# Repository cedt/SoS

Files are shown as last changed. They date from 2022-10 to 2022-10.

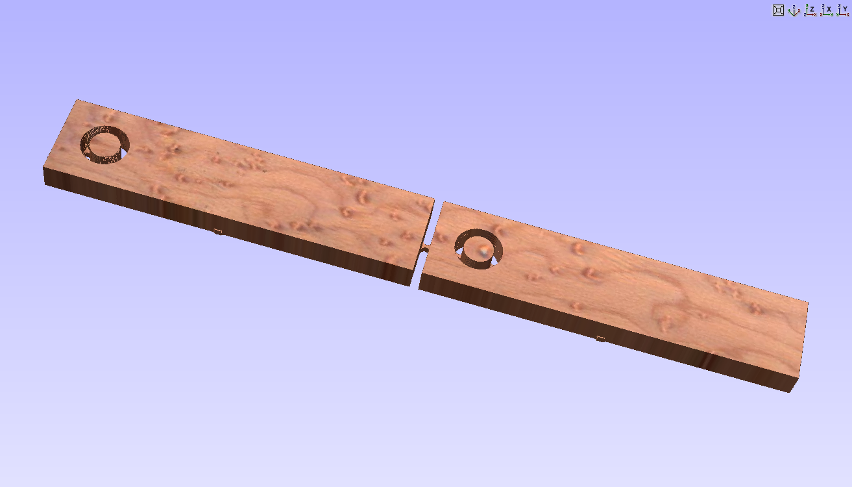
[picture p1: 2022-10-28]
Structure/Structure Type 1/via.png

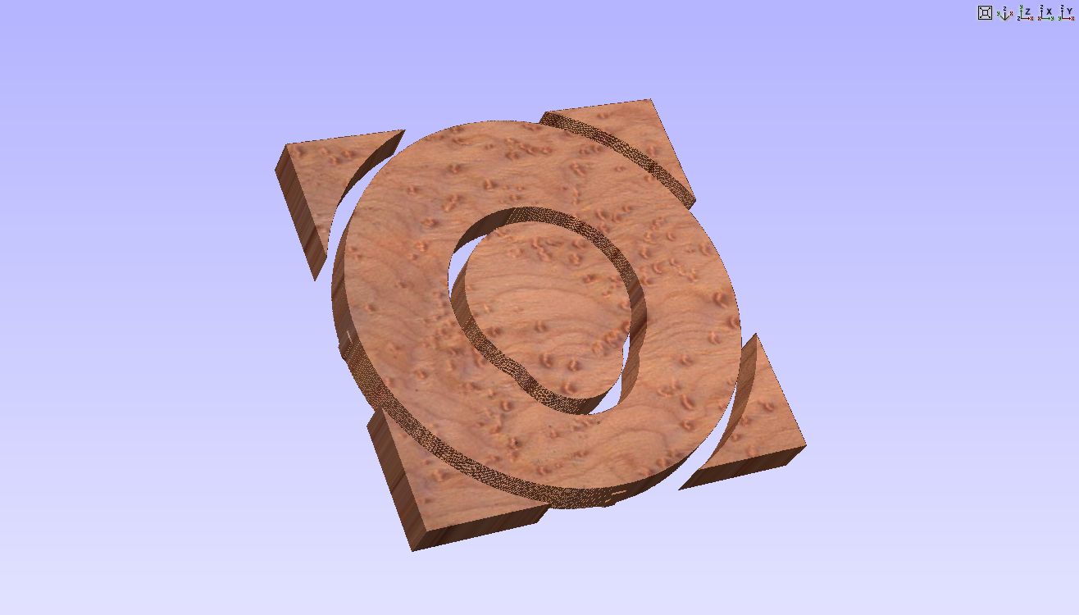
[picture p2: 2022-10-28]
Structure/Structure Type 1/flange.png

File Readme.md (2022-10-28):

# Science on a Stick 

---

### Folder Structure 
```
.
├── Arduino Code 				→ Contains code to be uploaded to Arduino 
│   └── SOS_Arduino_code
│       └── SOS_Arduino_code.ino
├── Arduino PCB and Hardware			→ Contains Schematic, BOM etc
│   ├── BOM-magnetic_switch_sos_v1-2022.pdf	→ Bill of Materials for Reed switch circuit
│   ├── BOM-ScienceonStick_V7-April2022.pdf	→ Bill of Materials for Main PCB
│   ├── Hardware_Acquisition_Sources.docx	→ Suggested sources to acquire components
│   ├── magnetic_switch_sos_v1-2022.sch 	→ Circuit for trigger switch
│   ├── photogate-sos-v2-2022.brd
│   ├── photogate-sos-v2-2022.sch
│   ├── ScienceOnStick_V7-April2022.brd
│   └── ScienceOnStick_V7-April2022.sch 	→ Circuit for main PCB
├── Images and Photographs
│   └── plots
│       └── ... plots created using experiments ... 
├── Python Code
│   ├── Analysis.ipynb
│   └── SoS_Acquisition.py
└── Structure
    ├── Structure Type 1
    │   ├── bar_inside.sbp
    │   ├── bar_outside.sbp
    │   ├── bars.crv
    │   ├── bars.png
    │   ├── base.crv
    │   ├── base_outside.sbp
    │   ├── base.png
    │   ├── flange.crv
    │   ├── flange_inner.sbp
    │   ├── flange_outside.sbp
    │   ├── flange.png
    │   ├── inside.sbp
    │   ├── via.crv
    │   ├── via_inside.sbp
    │   ├── via_outside.sbp
    │   └── via.png
    └── Structure Type 2
        ├── base.crv
        ├── base.png
        ├── correction.sbp
        ├── inside_baseandvia.sbp
        ├── outer_baseandvia.sbp
        ├── stand.crv
        ├── stand_in.sbp
        ├── stand_out.sbp
        ├── stand.png
        ├── via.crv
        ├── VIA-INNER.LOG
        ├── via-inner.sbp
        ├── VIA_OUTER.LOG
        ├── via_outer.sbp
        └── via.png
 ```

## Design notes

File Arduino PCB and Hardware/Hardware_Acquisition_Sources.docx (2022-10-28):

The Structural components of experimental setup can be made using household items such as cardboard, pipes and clothes pins. The electronic components can be acquired from places stated below:

The entire Science on a Stick experiment kit can be bought from https://store.sincgrid.com/index.php?route=product/product&path=71&product_id=108

Individual components can also be acquired as per convenience

1. Arduino Nano: https://www.sparkfun.com/products/15590, https://store-usa.arduino.cc/products/arduino-nano?selectedStore=us
2. Reed switch: https://www.sparkfun.com/products/8642
3. 2 pin Molex connector (M02 Connector): https://www.sparkfun.com/products/9918 (https://www.sparkfun.com/products/9918%20%20)
4. 3 pin Molex connector (M03 Connector): https://www.sparkfun.com/products/retired/9919
5. 36 SWG enamelled Copper wire: https://www.amazon.com/BNTECHGO-AWG-Magnet-Wire-Transformers/dp/B07JBQQR38/ref=sr_1_1_sspa?crid=P3E3WLDIDLN9&keywords=magnet+wire+32+awg&qid=1666948092&qu=eyJxc2MiOiIxLjg1IiwicXNhIjoiMS43MiIsInFzcCI6IjEuNDQifQ%3D%3D&sprefix=magnet+wire+32+aw%2Caps%2C335&sr=8-1-spons&psc=1
6. USB Type A to Mini B: https://www.adafruit.com/product/260
7. 12mm diameter Neodymium magnet: https://www.adafruit.com/product/9

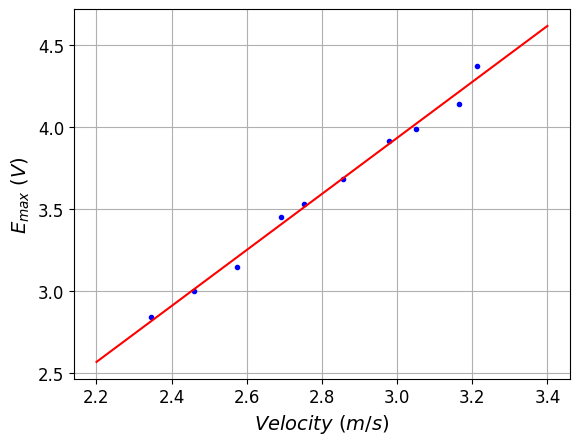
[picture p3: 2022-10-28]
Images and Photographs/plots/peak_V_vs_velocity.png

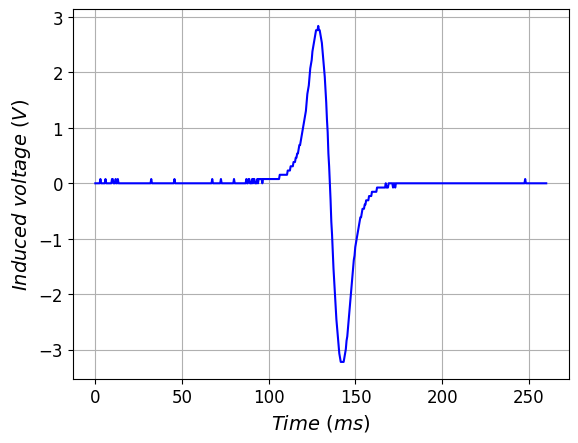
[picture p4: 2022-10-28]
Images and Photographs/plots/V_vs_t.png

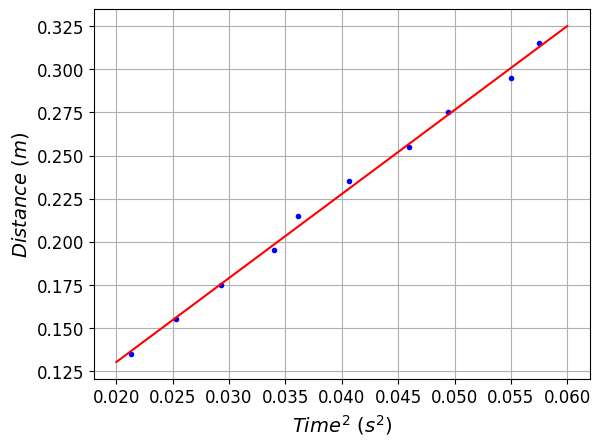
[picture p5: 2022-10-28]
Images and Photographs/plots/distance_vs_t2.png

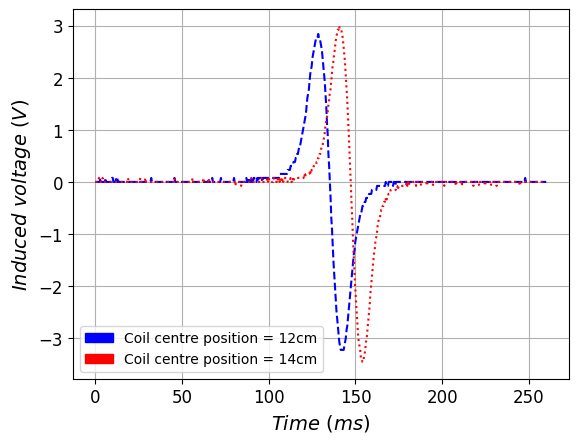
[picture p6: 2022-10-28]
Images and Photographs/plots/V_vs_t_compare.png

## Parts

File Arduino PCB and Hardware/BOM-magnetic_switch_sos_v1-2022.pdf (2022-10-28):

# Bill of Material for Magnetic Switch

Part | Value | Device | Package
LED1 | RED | LED3MM | LED3MM
P-ON | RED | LED3MM | LED3MM
R1 | 1K | RESISTOR | 0207/7 (1/8 Watt)
R2 | 1K | RESISTOR | 0207/7 (1/8 Watt)
R3 | 4.7k | RESISTOR | 0207/7 (1/8 Watt)
S1 | NA | Reed Switch
SL1 | NA | M03-Connector | Male Connector. Right Angle

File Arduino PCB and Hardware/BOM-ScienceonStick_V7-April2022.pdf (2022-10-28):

# Bill of Material for Science on a Stick Arduino Board

Part | Value | Device | Package
C1 | 0.1uF | Ceramic CAPACITOR | C025-025X050
C3 | 0.1uF | Ceramic CAPACITOR | C025-025X050
C4 | 10uF | Electrolytic CAPACITOR | E2,5-6
C5 | 10uF | Electrolytic CAPACITOR | E2,5-6
IC1 | LM358N | LM358N | DIL08
LED1 | RED | LED3MM | LED3MM
LED2 | RED | LED3MM | LED3MM
TOP-SWITCH | NA | M03-Connector | Male Connector
R1 | 680 | RESISTOR | 0207/7 (1/8 Watt)
R2 | 10k | RESISTOR | 0207/7 (1/8 Watt)
R3 | 47k | RESISTOR | 0207/7 (1/8 Watt)
R4 | 47k | RESISTOR | 0207/7 (1/8 Watt)
R5 | 1k | RESISTOR | 0207/7 (1/8 Watt)
R6 | 10k | RESISTOR | 0207/7 (1/8 Watt)
R8 | 4.7k | RESISTOR | 0207/7 (1/8 Watt)
BOTTOM-SWITCH | NA | M03-Connector | Male Connector
S1 | NA | Omron Push-Button | 40-XX
SL1 | NA | 2-pin header | Straight
SL2 | NA | 2-pin header | Straight
COIL | NA | M02-Connector | Male Connector
SL4 | NA | 2-pin header | Straight
U$1 | NA | ARDUINO_NANO | ARDUINO_NANO

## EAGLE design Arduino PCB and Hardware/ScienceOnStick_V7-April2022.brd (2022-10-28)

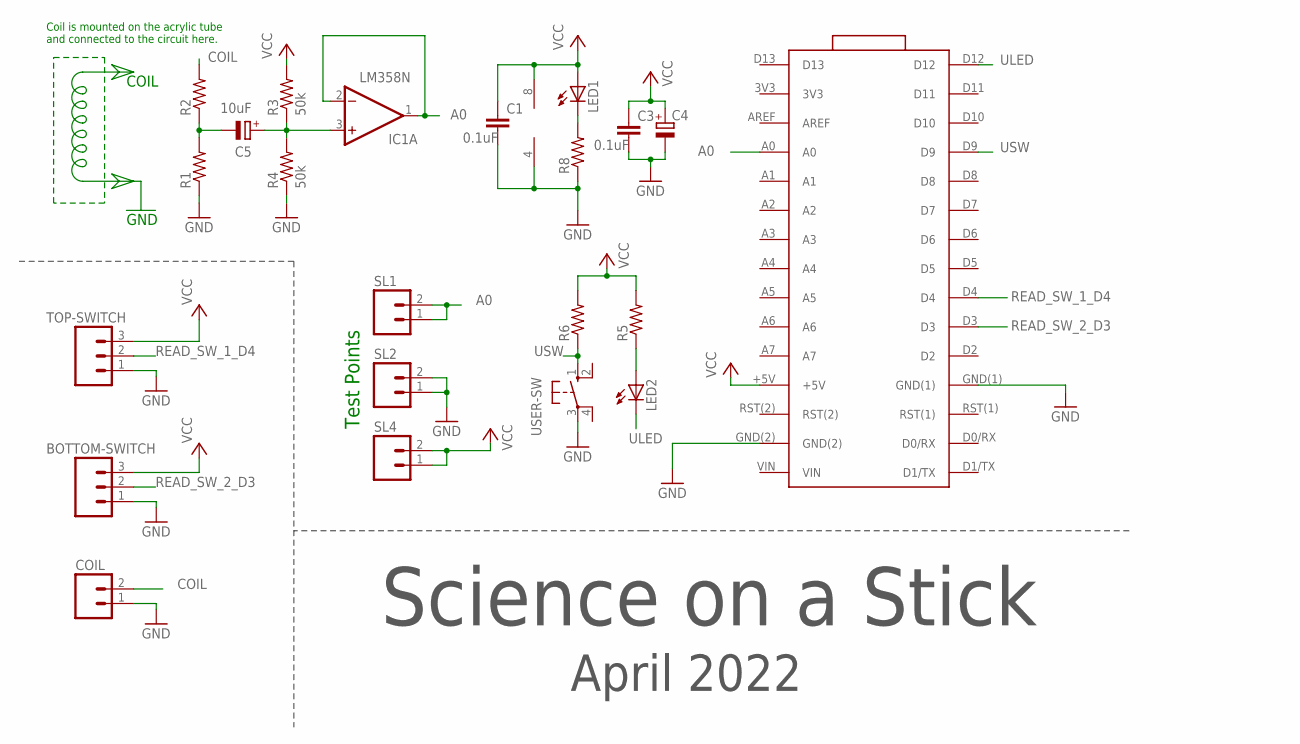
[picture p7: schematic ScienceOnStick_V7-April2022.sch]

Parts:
BOTTOM-SWITCH: M03; 03P
C1, C3: 0.1uF; C025-025X050
C4: CPOL-EUE2.5-6; E2,5-6
C5: 10uF; E2,5-6
COIL: M02; 02P
IC1: LM358N; DIL08
LED1, LED2: LED3MM
R1, R2, R5, R6, R8: RESISTOR0207/7; 0207/7
R3, R4: 50k; 0207/7
SL1, SL2, SL4: M02; 02P
TOP-SWITCH: M03; 03P
U$1: ARDUINO_NANO_3_ARDUINO(NANO_3.0); ARDUINO_NANO_3_ARDUINO_NANO_30PIN
USER-SW: 40-XX; B3F-40XX

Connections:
A0: IC1.1 (OUT), IC1.2 (-IN), SL1.1, SL1.2, U$1.A0
CLAMP_SIGNAL: C5.+, IC1.3 (+IN), R3.1, R4.2
COIL: COIL.2, R2.2
GND: BOTTOM-SWITCH.1, C1.2, C3.2, C4.-, COIL.1, IC1.4 (V-), R1.1, R4.1, R8.1, SL2.1, SL2.2, TOP-SWITCH.1, U$1.GND(1), U$1.GND(2), USER-SW.3
unnamed: C5.-, R1.2, R2.1
unnamed: LED2.A, R5.1
unnamed: LED1.K (C), R8.2
READ_SW_1_D4: TOP-SWITCH.2, U$1.D4
READ_SW_2_D3: BOTTOM-SWITCH.2, U$1.D3
ULED: LED2.K (C), U$1.D12
USW: R6.1, U$1.D9, USER-SW.1 (S)
VCC: BOTTOM-SWITCH.3, C1.1, C3.1, C4.+, IC1.8 (V+), LED1.A, R3.2, R5.2, R6.2, SL4.1, SL4.2, TOP-SWITCH.3, U$1.+5V

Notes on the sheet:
Science on a Stick
April 2022
Coil is mounted on the acrylic tube and connected to the circuit here.
COIL
GND
Test Points

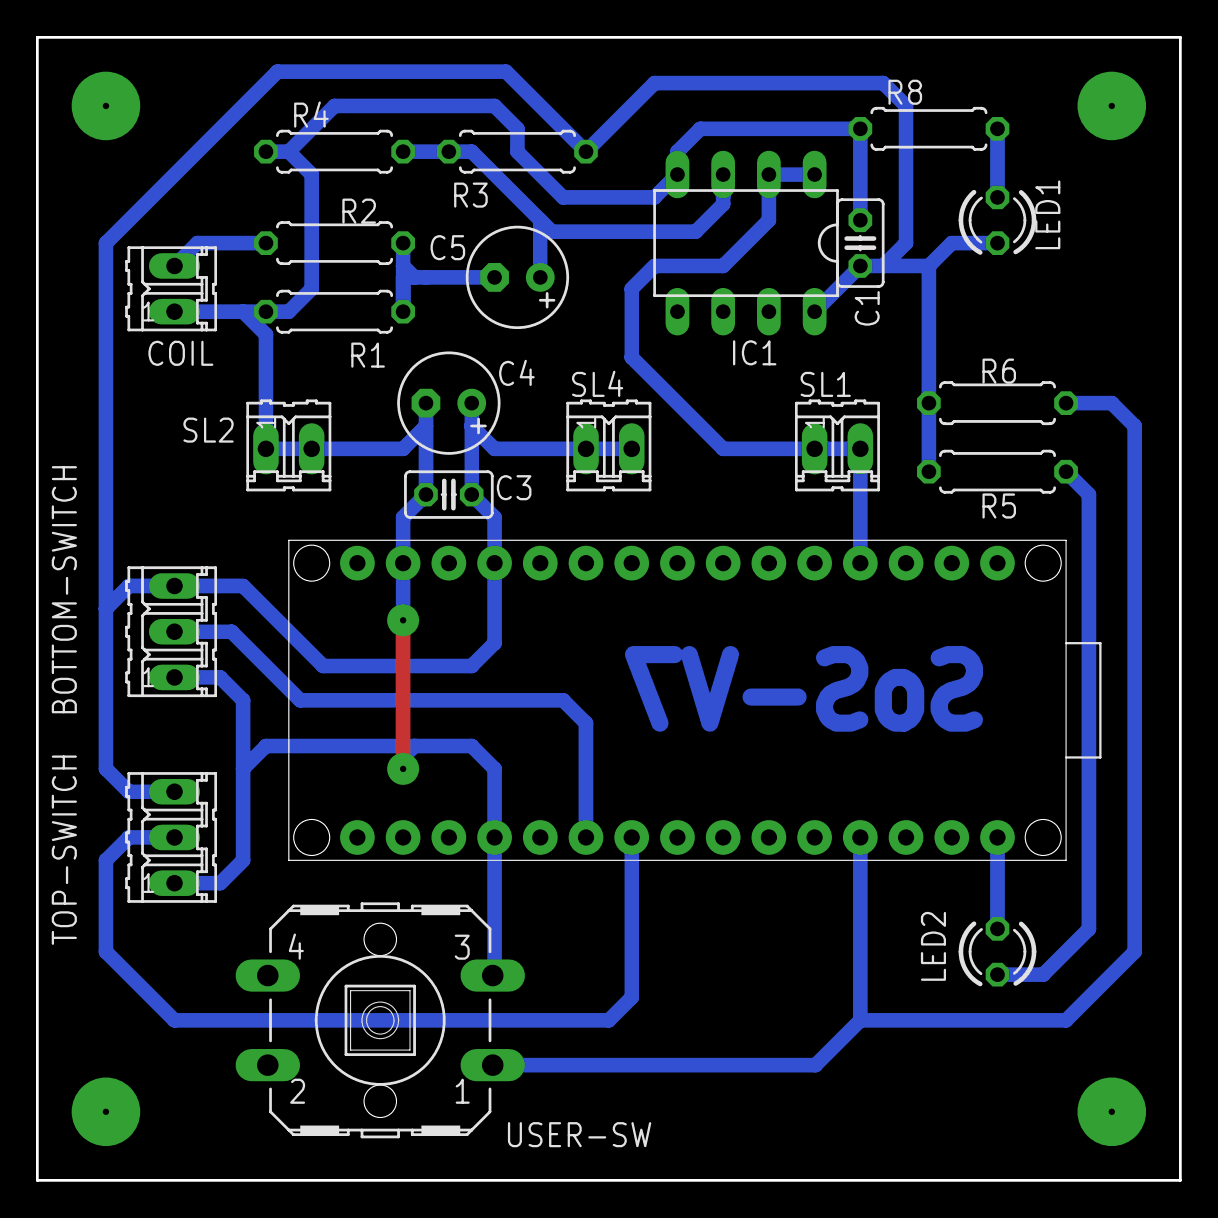
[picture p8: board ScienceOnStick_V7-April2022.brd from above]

Board: 2 copper layers, 63.5 x 63.5 mm, 22 parts (0 on the bottom side), 12 nets.

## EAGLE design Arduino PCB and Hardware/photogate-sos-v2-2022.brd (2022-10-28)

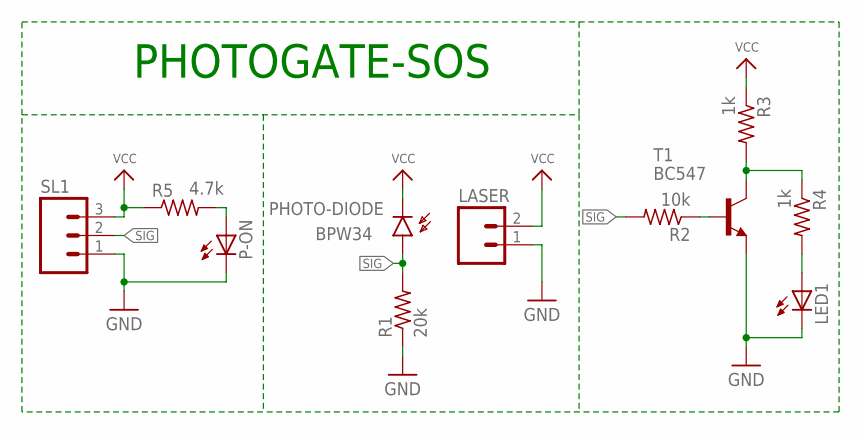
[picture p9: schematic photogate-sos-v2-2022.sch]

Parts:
LASER: M02; 02P
LED1: LED3MM
P-ON: LED3MM
PHOTO-DIODE: BPW34; BPW32
R1: 20k; 0204/7
R2: 10k; 0204/7
R3, R4: 1k; 0204/7
R5: 4.7k; 0204/7
SL1: M03; 03P
T1: BC547; TO92

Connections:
GND: LASER.1, LED1.K (C), P-ON.K (C), R1.1, SL1.1, T1.1 (E)
unnamed: R2.1, T1.2 (B)
unnamed: R3.2, R4.1, T1.3 (C)
unnamed: LED1.A, R4.2
unnamed: P-ON.A, R5.2
SIG: PHOTO-DIODE.A, R1.2, R2.2, SL1.2
VCC: LASER.2, PHOTO-DIODE.K (C), R3.1, R5.1, SL1.3

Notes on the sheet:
PHOTOGATE-SOS

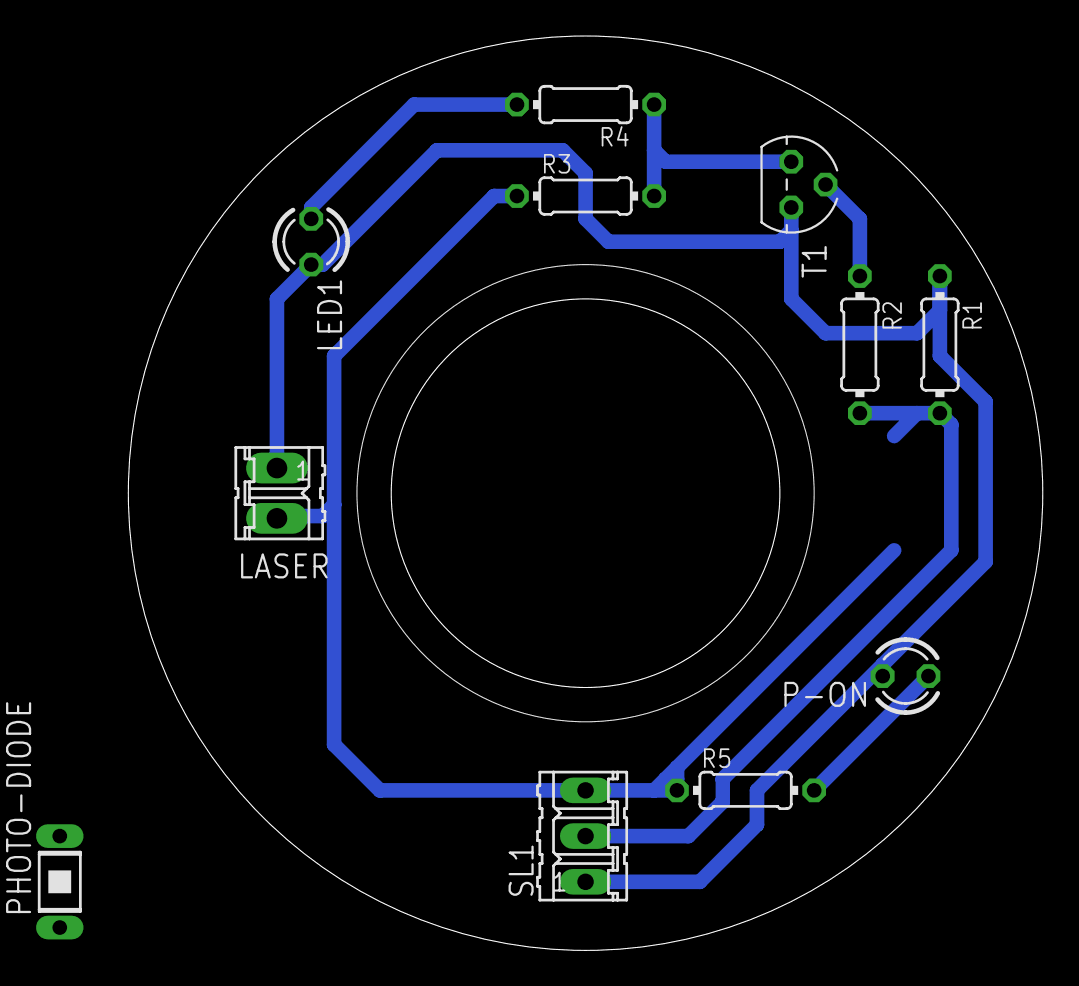
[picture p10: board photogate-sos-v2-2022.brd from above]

Board: 2 copper layers, 50.8 x 50.8 mm, 11 parts (0 on the bottom side), 7 nets.

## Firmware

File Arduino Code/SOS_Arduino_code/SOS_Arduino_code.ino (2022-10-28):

/*
 * Program by Harsh Sharma at TI-CEPD Lab at NSUT
 * To be run on a Arduino/ Arduino compatible device with digital and Analog input pins and supporting 
 * Serial communication at 115200 baudrate
 * Also, Setup to acquire readings is required, to get more info refer to Science on a Stick experiment description
 * 
 * 3 input pins required, 1 analog and 2 digital
 * Analog pin is to read coil data
 * digital pins are used to trigger starting and stopping reading data
*/

#define pin1 A0       //Arduino analog pin to which coil is connected
#define pin2 4        //Arduino digital pin to which top trigger is connected
#define pin3 3        //Arduino digital pin to which bottom trigger is connected

//Pins for on-board LED
#define led_vcc 12
#define led_gnd 10


long int t1;          //variable to hold start time of readings

void setup(){
  
  //Serial initialized to 115200 baudrate, this matches with the value used by Data Acquisition program
  Serial.begin(115200);
  
  //Set analog pin as input for reading voltage induced through coil
  pinMode(pin1,INPUT);
  
  //Set digital pins as input for reading top and bottom trigger of the SoS apparatus
  pinMode(pin2,INPUT);
  pinMode(pin3,INPUT);
  
  //Set LED as Output 
  pinMode(led_vcc,OUTPUT);
  pinMode(led_gnd,OUTPUT);
  digitalWrite(led_vcc,HIGH);
  digitalWrite(led_gnd,LOW);
}
 
void loop(){
  
  //Wait until top trigger is triggered, after which coil data is read
  while(true){
    //When using hall effect sensor in pullup, change digitalRead(pin2) == LOW 
    //when using standard reed switch, change it to digitalRead(pin2) == HIGH
    if(digitalRead(pin2)==LOW){  //Top trigger hit condition
      t1=millis();                //Store current time as readings start time
      break;
    }
  }
  
  //Read coil data until bottom trigger is triggered
  while(true){
    if(digitalRead(pin3)==LOW){  //Bottom trigger hit condition
        for(int i=0;i<30;i++)
          Serial.println(analogRead(pin1));
          
        Serial.println("3000");   //Send End-Of-Data symbol

        //Send start and end time for readings
        Serial.println(t1);
        Serial.println(millis());
        break;    
      }
      else{
        Serial.println(analogRead(pin1));   //Continuously send data over Serial
      }
  }

  //delay between each reading
  delay(5000);
}

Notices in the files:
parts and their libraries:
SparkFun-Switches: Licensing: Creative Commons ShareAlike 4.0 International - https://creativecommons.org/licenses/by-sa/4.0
